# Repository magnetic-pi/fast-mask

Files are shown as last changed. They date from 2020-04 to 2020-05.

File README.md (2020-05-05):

# F.A.S.T Mask

Filter Adapted Snorkel Tube (F.A.S.T) Mask <br />
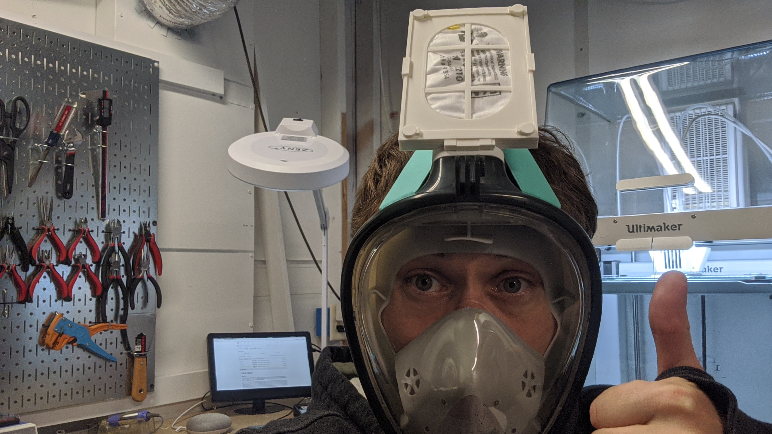
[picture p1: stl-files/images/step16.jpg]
        

#### Objective

The **Filter Adapted Snorkel Tube** (F.A.S.T) Mask is an attempt to help ease the burden facing medical staff around the world due to the shortage of face shields, eye protection, and N95 masks. The goal of this project was to find easy to obtain parts and modify them to provide a cheap reusable (PPE) mask solution.

The F.A.S.T project modifies an existing snorkel mask, so that a PM2.5, N95, P95 or other similar filters can be easily retrofitted to a modified snorkel tube. F.A.S.T provides an added advantage, as the filter masks are no longer touching a user's face directly, which helps to preserve the filters. Doctors and nurses are currently required to use the face masks for a days at a time, and that's if they are lucky enough to have access to a mask at all. The F.A.S.T solution could potentially provide a way to immediately double existing filter supplies on location, as well as increase/improve filter reusability and sharing. The F.A.S.T adapter provides an easily maintainable and reusable face shield solution for front line responders. Due to its modularity, the various parts of F.A.S.T can be quickly disassembled, sanitized, reused, and replaced. The various types of masks (N95, PM2.5) never directly touch the users face, therefore making it so masks can easily be sterilized in accordance to [sterilization studies](https://news.ycombinator.com/item?id=22680799) and reused.

Currently the Covid-19 virions are about 0.125 microns in size. This means that the PM2.5 filter may not completely protect users, however, neither will wearing an improperly fitted P95/N95 masks which often have leaks based on fit to the face. The F.A.S.T Mask also provides enhanced protection by eliminating the gaps typically found when wearing separate N95 masks, face shields, and eye protection.

This project was inspired by and is dedicated to [Dr. Usama Riaz](https://old.reddit.com/r/HumansBeingBros/comments/fnwflk/dr_usama_riaz_has_spent_weeks_screening_treating/) and the many other selfless heroes around the world who are on the front lines fighting the good fight against Covid-19.

#### Design Objectives
1. Protect users' entire face.
2. Keep the filter as isolated and clean as possible. (No facial oil contamination and mitigate direct body fluid exposure.)
3. No tooling required.
4. Easy sterilization.
5. Reusability.
6. Parts must be easily acquirable globally.
7. Provide a consistent seal between the filter and filter holder.
    
#### Build Steps
The build steps can be found in: [stl-files/INSTRUCTIONS.md](https://github.com/magnetic-pi/fast-mask/blob/master/stl-files/INSTRUCTIONS.md).

#### Licensing
The F.A.S.T components are free and open source to ensure the interoperability of F.A.S.T with various mask vendors, and to encourage rapid development by others.

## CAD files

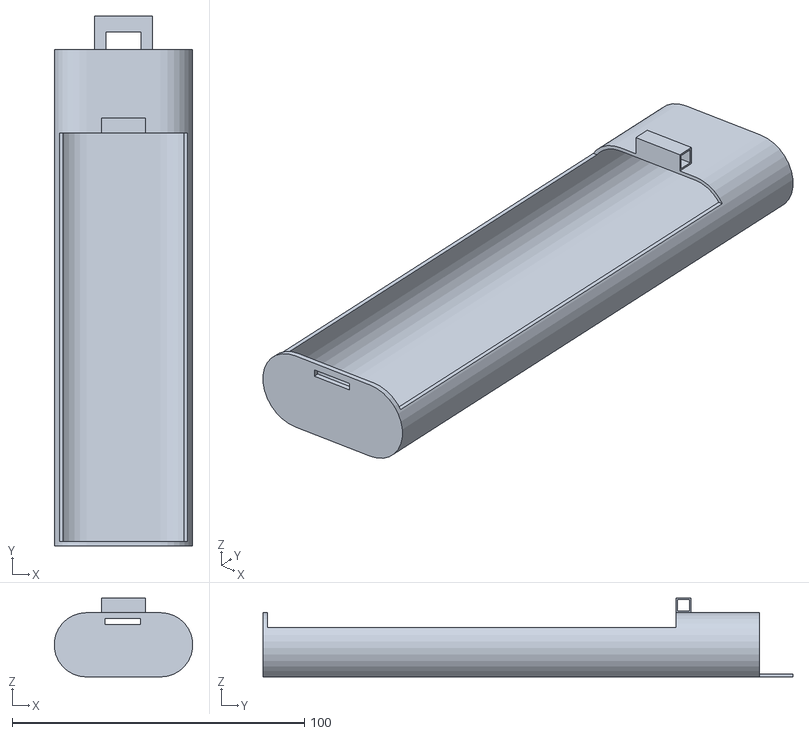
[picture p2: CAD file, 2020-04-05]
stl-files/universal-filter-mask-stl-files/snorkel-tube-connector.stl
47.4 x 181.5 x 27.0

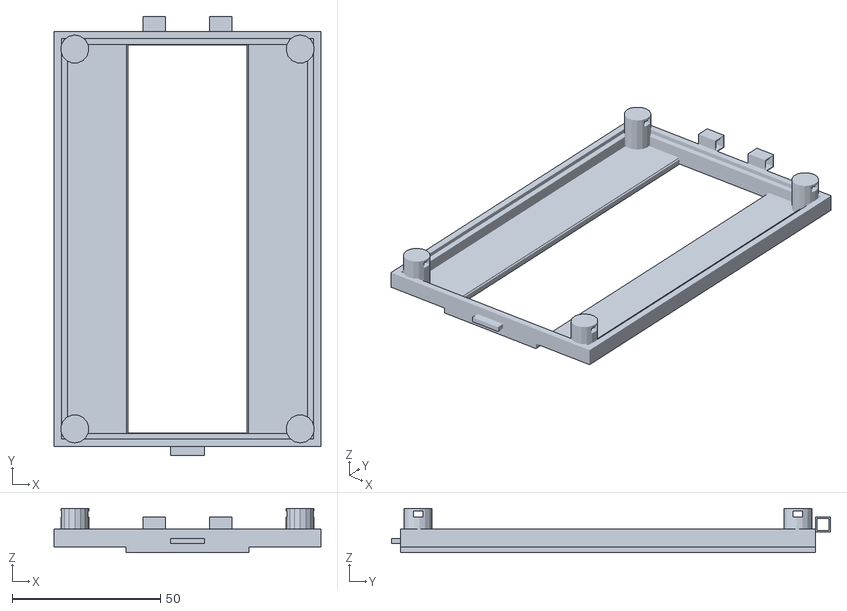
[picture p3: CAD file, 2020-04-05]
stl-files/universal-filter-mask-stl-files/filter-holder-bottom.stl
90.0 x 148.0 x 15.0

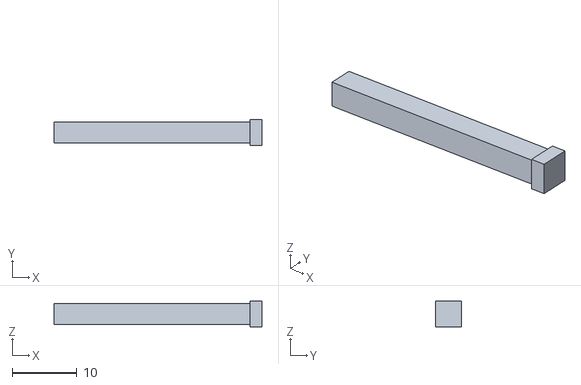
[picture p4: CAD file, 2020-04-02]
stl-files/universal-filter-mask-stl-files/connector-block-peg.stl
32.0 x 4.00 x 4.00

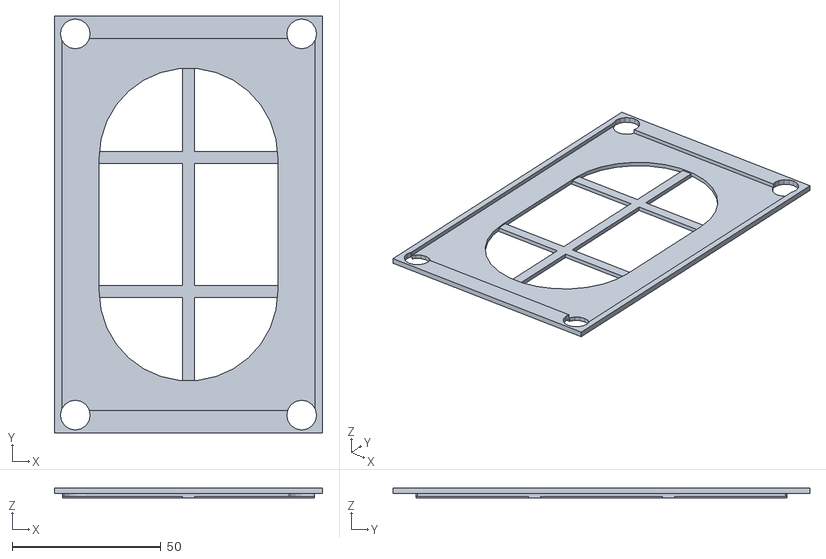
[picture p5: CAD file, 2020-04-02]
stl-files/universal-filter-mask-stl-files/universal-filter-holder.stl
90.0 x 140.0 x 3.50

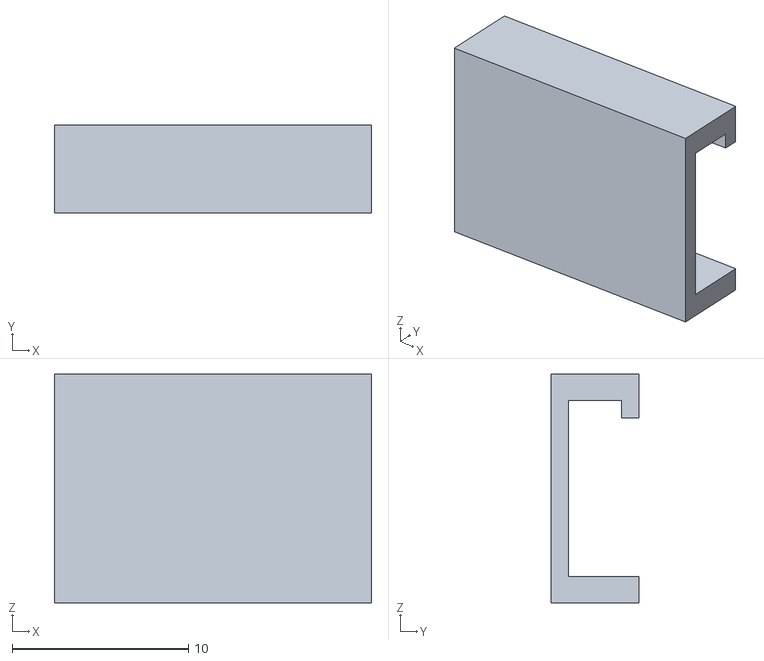
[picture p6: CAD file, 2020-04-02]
stl-files/universal-filter-mask-stl-files/filter-side-clamps.stl
18.0 x 5.00 x 13.0

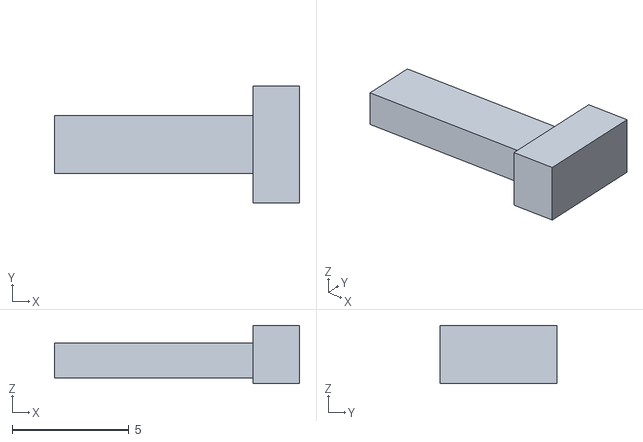
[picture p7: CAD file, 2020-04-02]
stl-files/universal-filter-mask-stl-files/peg-connector-clip.stl
10.5 x 5.00 x 2.50

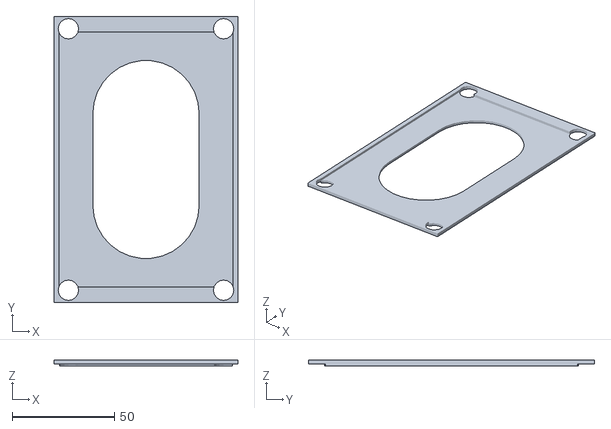
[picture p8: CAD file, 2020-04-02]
stl-files/universal-filter-mask-stl-files/front-plug.stl
90.0 x 140.0 x 3.00

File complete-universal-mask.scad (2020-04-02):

/////////////////////////////////////////////////////////////////////////
// The universal mask is made with a filter holder specifically        //
// designed to have a smaller opening to hold partial piece of a mask. //
// This should only be used in times of emergency when supplies are    //
// critically low.                                                     //
/////////////////////////////////////////////////////////////////////////


use <scad-parts/snorkel-tube-attachment.scad>
use <scad-parts/filter-holder-bottom.scad>
use <scad-parts/connector-pegs.scad>
use <scad-parts/connector-blocks.scad>
use <scad-parts/universal-filter-holder-top.scad>
use <scad-parts/front-plug.scad>
use <scad-parts/filter-side-clamps.scad>

/////////////////////////////////////////////////////
// Filter layer bottom.                            //
//use <scad-parts/filter-holder-bottom.scad>       //
/////////////////////////////////////////////////////
translate([0,1.5,-5])
filter_holder_bottom(filter_holder_top_x=90,
                     filter_holder_top_y=140,
                     filter_holder_top_z=6,
                     snorkel_diameter=25.5,
                     snorkel_tube_height=5,
                     snorkel_tube_radius=11,
                     peg_y_position=38,
                     peg_space=64,
                     number_of_pegs=2,
                     peg_height=12,
                     peg_radius=5,
                     connector_clip_x=16,
                     connector_clip_y=3,
                     connector_clip_z=2);

///////////////////////////////////////////////////////
// Universal first filter holder layer.              //
//use <scad-parts/universal-filter-holder-top.scad>  //
///////////////////////////////////////////////////////
//color("green")
//translate([0,11.50,-1])
//universal_filter_holder(filter_holder_x=90,
//              filter_holder_y=140,
//              filter_holder_z=2,
//              filter_hole_height = 6,
//              filter_hole_radius = 30,
//              filter_hole_length = 45,
//              peg_y_position=38,
//              peg_space=64,
//              number_of_pegs=2,
//              peg_height=10,
//              peg_radius=5,
//              connector_clip_x=10,
//              connector_clip_y=3,
//              connector_clip_z=2);

//////////////////////////////////////////////////////
// Universal second filter holder layer.            //
//use <scad-parts/universal-filter-holder-top.scad> //
//////////////////////////////////////////////////////
//color("red")
//translate([0,11.50,1])
//universal_filter_holder(filter_holder_x=90,
//              filter_holder_y=140,
//              filter_holder_z=2,
//              filter_hole_height = 6,
//              filter_hole_radius = 30,
//              filter_hole_length = 45,
//              peg_y_position=38,
//              peg_space=64,
//              number_of_pegs=2,
//              peg_height=10,
//              peg_radius=5,
//              connector_clip_x=10,
//              connector_clip_y=3,
//              connector_clip_z=2);

//////////////////////////////////////////////////
// Connector tube to snorkel mask.              //
//use <scad-parts/snorkel-tube-attachment.scad> //
//////////////////////////////////////////////////
rotate([0,0,0])
translate([0, 0, -5])
snorkel_filter_attachment_tube(snorkel_diameter=25.5, snorkel_tube_height=170, snorkel_tube_radius=11);

///////////////////////////////////////////
// Clips for four filter holder pegs.    //
// use <scad-parts/connector_pegs.scad>  //
///////////////////////////////////////////
//peg_connector_clip(connector_clip_x=10,
//                   connector_clip_y=2.5,
//                   connector_clip_z=1.5);

///////////////////////////////////////////
// Peg for front holder squares.         //
//use <scad-parts/connector_blocks.scad> //
///////////////////////////////////////////
//connector_block_peg(ccube_x=30, 
//                     ccube_y=4,
//                     ccube_z=4);

///////////////////////////////////////////////
// Side clamps for preventing side buldging. //
//use <scad-parts/filter-side-clamps.scad>   //
///////////////////////////////////////////////
//filter_side_clamps();

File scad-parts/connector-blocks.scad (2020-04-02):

//////////////////////////////////////////////////////////////////////////////////////////////
// This module is used for connecting the snorkel to the filter.//
//////////////////////////////////////////////////////////////////////////////////////////////

// Generates two BLUEoutside blocks for the plug to connect through.
module connector_block_cutout(ccube_x, ccube_y, ccube_z){
    color("blue")
    difference() {
        cube([ccube_x, ccube_y, ccube_z],center=true);
        cube([ccube_x+2, ccube_y-1, ccube_z-1],center=true);
    }
}

// Generates RED inside block for the plug to connect through.
module connector_block_outsides(ccube_x, ccube_y, ccube_z){
    color("red")
    difference() {
        connector_block_cutout(ccube_x, ccube_y, ccube_z);
        cube([ccube_x-15, ccube_y+2, ccube_z+2],center=true);
    }
}

// Generates the white plug to hold the parts together.
module connector_block_peg(ccube_x, ccube_y, ccube_z){
    color("white")
    difference() {
        cube([ccube_x+2, ccube_y, ccube_z],center=true);
        translate([-1, 0, 0])
        connector_block_cutout(ccube_x+.25, ccube_y+.25, ccube_z+.25);
    }
}

// Generates two BLUEoutside blocks for the plug to connect through.
connector_block_outsides(ccube_x=30, ccube_y=5, ccube_z=5);

// Generates RED inside block for the plug to connect through.
connector_block_cutout(ccube_x=15, ccube_y=5, ccube_z=5);

// Generates the white plug to hold the parts together.
//connector_block_peg(ccube_x=30, ccube_y=5, ccube_z=5);

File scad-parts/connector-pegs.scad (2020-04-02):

//////////////////////////////////////////////////////////////////
// This module is used for generating the peg cutouts and pegs. //
//////////////////////////////////////////////////////////////////

// peg_space: This controls the X-axis space between the pegs.
// number_of_pegs: This defines the number of pegs to generate.
// peg_height: This defines the Z-axis height of the peg.
// peg_radius: This determines the diameter/circumferance of each peg.
// peg_y_position: This determines the Y-axis position of the pegs.

// This generates the GREEN peg clip.
module peg_connector_clip(connector_clip_x, connector_clip_y, connector_clip_z) {
    color("green")
    cube([connector_clip_x, connector_clip_y, connector_clip_z],true);
    translate([connector_clip_y+2,0,.25])
    cube([2,5,2.5],true);
}

// This generates the WHITE hole size in the Blue peg so the GREEN clip can slide in.
module peg_connector_hole(connector_clip_x, connector_clip_y, connector_clip_z) {
    color("white")
    peg_connector_clip(connector_clip_x+.25, connector_clip_y+.25, connector_clip_z);
}

// This module combines and diffs the WHITE hole from the BLUE peg.
module peg(peg_height, peg_radius, connector_clip_x, connector_clip_y, connector_clip_z) {
    difference() {
        // This generates the BLUE peg.
        color("blue")
        cylinder(h = peg_height, r1 = peg_radius, r2 = peg_radius, center = true);
        
        // This is the WHITE peg Hole.
        rotate([0,0,90])
        translate([2, 0, +4])
        peg_connector_hole(connector_clip_x, connector_clip_y, connector_clip_z);
    }
}

// This module generates "number_of_pegs" at "pegs_space" in millimeters apart.
module holder_pegs(peg_space, number_of_pegs, peg_height, peg_radius, connector_clip_x, connector_clip_y, connector_clip_z) {
    for (i=[0: 360/number_of_pegs: 360])
        rotate([0,0,i])
        translate([peg_space,0,0])
        peg(peg_height, peg_radius, connector_clip_x, connector_clip_y, connector_clip_z);
}


peg_y_position=20;

translate([0,peg_y_position,0])
holder_pegs(peg_space=60,
            number_of_pegs=2,
            peg_height=12,
            peg_radius=5,
            connector_clip_x=13,
            connector_clip_y=3,
            connector_clip_z=2);

//translate([0,-peg_y_position,0])
//holder_pegs(peg_space=60,
//            number_of_pegs=2,
//            peg_height=12,
//            peg_radius=5,
//            connector_clip_x=10,
//            connector_clip_y=3,
//            connector_clip_z=2);

//peg_connector_clip(connector_clip_x=10,
//                   connector_clip_y=3,
//                   connector_clip_z=2);

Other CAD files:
scad-parts/filter-holder-bottom.scad
scad-parts/filter-side-clamps.scad
scad-parts/front-plug.scad
scad-parts/snorkel-tube-attachment.scad
scad-parts/universal-filter-holder-top.scad

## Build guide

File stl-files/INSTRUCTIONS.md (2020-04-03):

# F.A.S.T Mask Assembly Instructions

### Overview
These directions assume that filter (N95, P95, PM2.5) masks will need to be altered to fit in the filter holders correctly. Ideally 3M or some other manufactures would be able create a flat filter much like the PM2.5 filter [here](https://www.amazon.com/Filters-Replacement-Running-Cycling-Activities/dp/B086GS2NBW/ref=sr_1_6?crid=T60BPNRLF9CD&dchild=1&keywords=pm2.5+mask+replacement+filters&qid=1585763601&sprefix=pm2.5+mask+replacement+%2Caps%2C211&sr=8-6) so that cutting a filter masks would no longer be required. The steps outlined in this document will guide users through the process for altering a N95 mask so that it will work with the F.A.S.T appliance.

### Requirements
1. Snorkel Mask ([Amazon Link](https://www.amazon.com/Knit-Outdoor-Panoramic-Anti-Fog-Anti-Leak/dp/B079FL6W4C))
2. PM2.5 Activated Carbon Filter ([Amazon Link](https://www.amazon.com/gp/product/B086634MWS))
3. N95 or P95 Mask. (Currently out everywhere!)
4. All parts have been printed from [stl-files/universal-filter-mask-stl-files/](https://github.com/magnetic-pi/fast-mask/tree/master/stl-files/universal-filter-mask-stl-files) directory:

    * Modified Snorkel tube attachment. (Print 1)
    * Filter Holders. (Print 2)
    * Bottom Filter Holder. (Print 1)
    * Connector Pegs. (Print 4)
    * Connector Block Peg. (Print 1)

### Build Steps
1. Grab a N95 mask. <br />
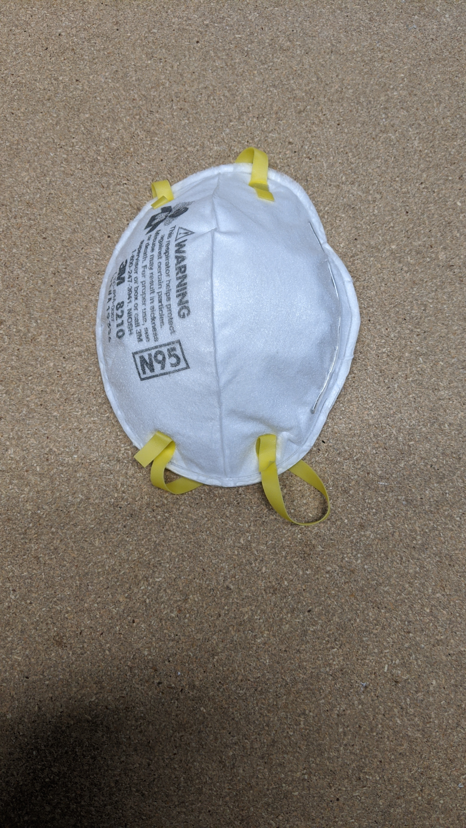
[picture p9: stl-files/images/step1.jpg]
    

2. Remove any straps on the outside of the mask.<br />
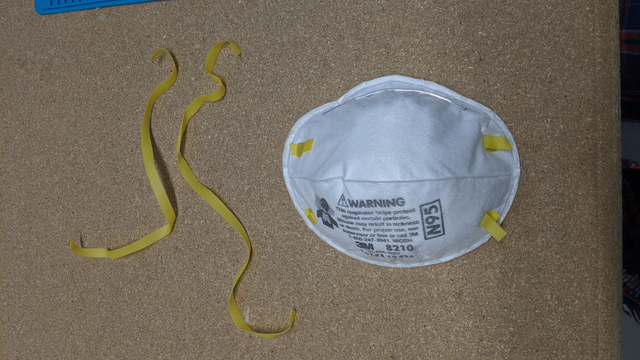
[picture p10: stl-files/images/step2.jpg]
    
    
3. Cut the mask in half.<br />
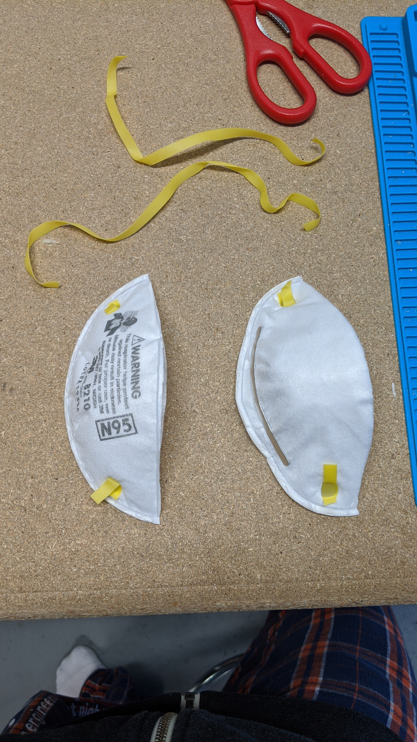
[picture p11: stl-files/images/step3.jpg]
    
    
4. Cut off the two ends so that the mask fits in the filter holder ensuring the hole is covered correctly.<br />
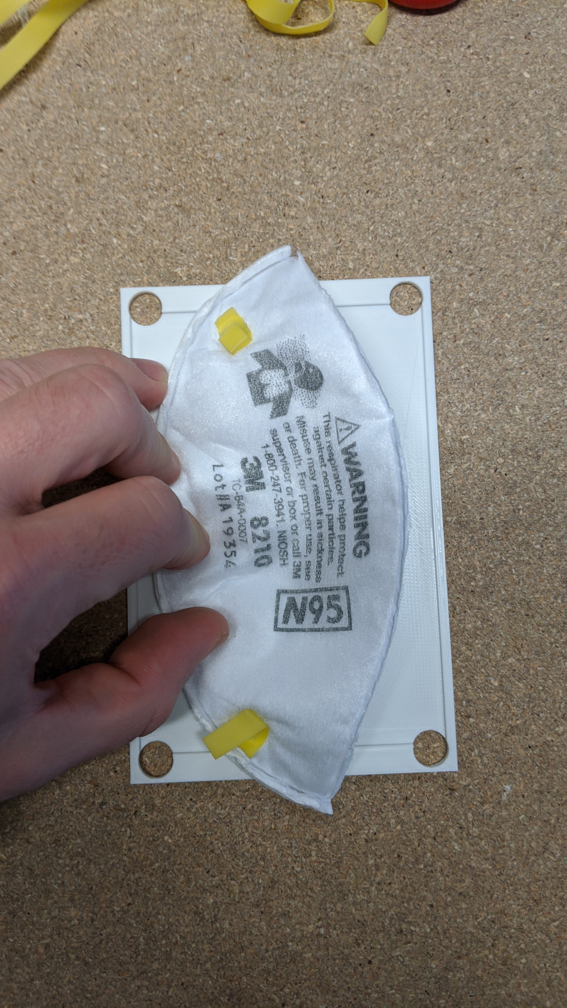
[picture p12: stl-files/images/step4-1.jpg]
    
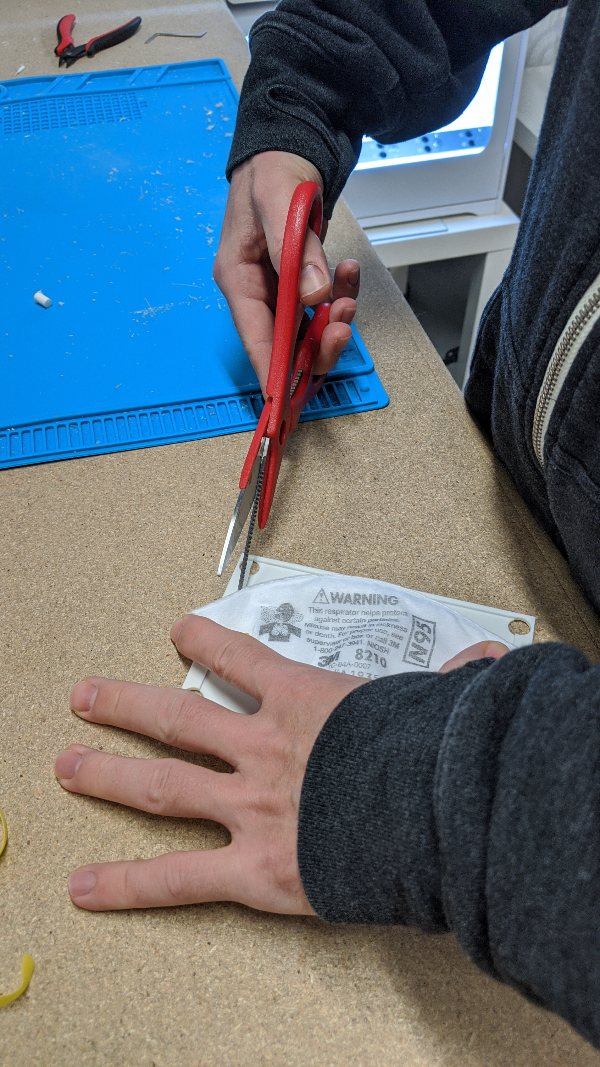
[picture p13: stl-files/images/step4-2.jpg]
    

5. Lay out the F.A.S.T parts.<br />
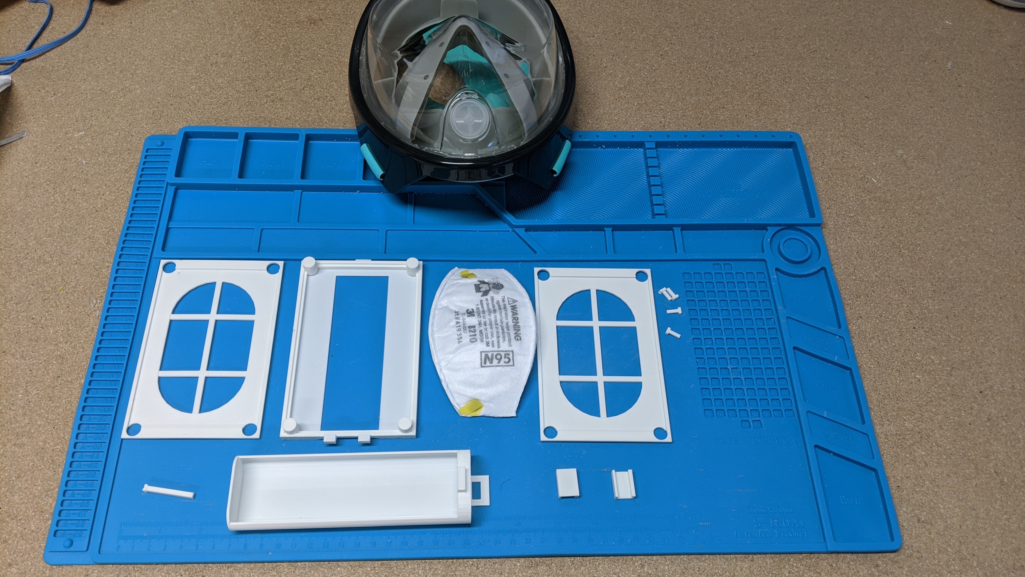
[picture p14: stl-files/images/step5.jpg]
   

6. Attach the filter holder pieces to the filter bottom.<br />
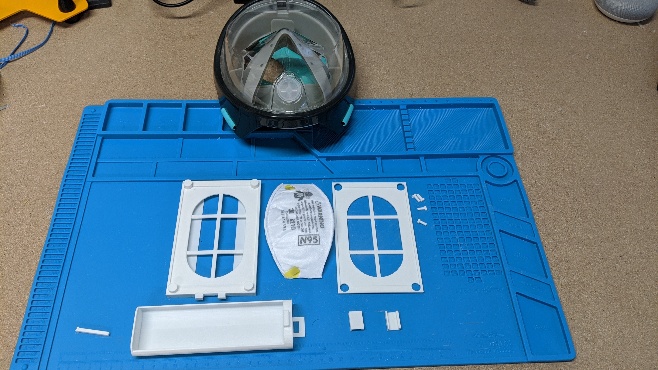
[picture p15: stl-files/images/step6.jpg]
    
    
7. Place filter on top of the first filter holder, making sure to completely cover the opening below it.<br />
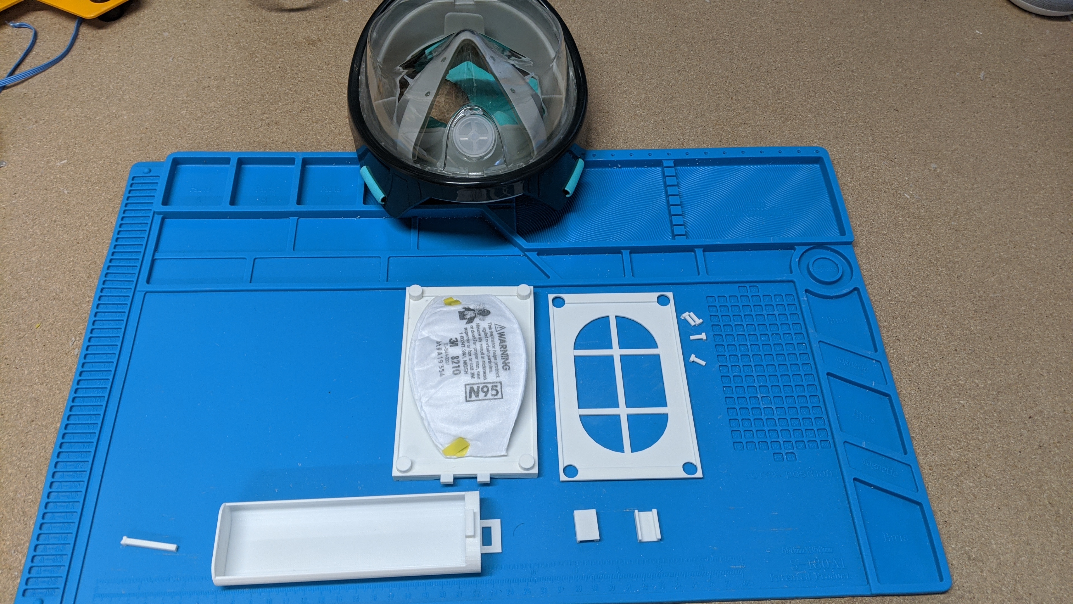
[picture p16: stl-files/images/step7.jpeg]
    
    
8. Attach the second filter holder piece on top.<br />
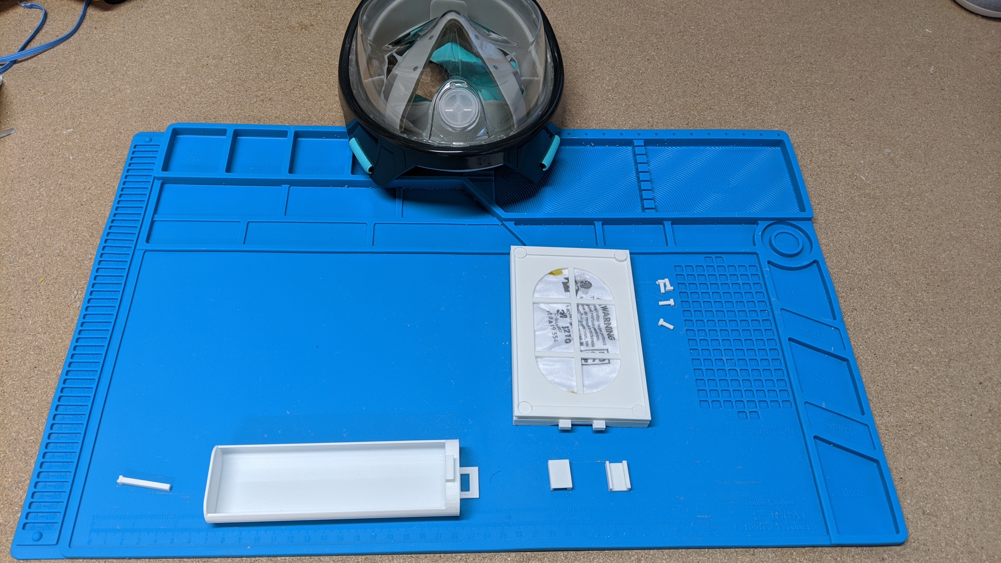
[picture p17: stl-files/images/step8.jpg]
    
    
9. Insert the filter holder pins into the four round pegs in the corners.<br />
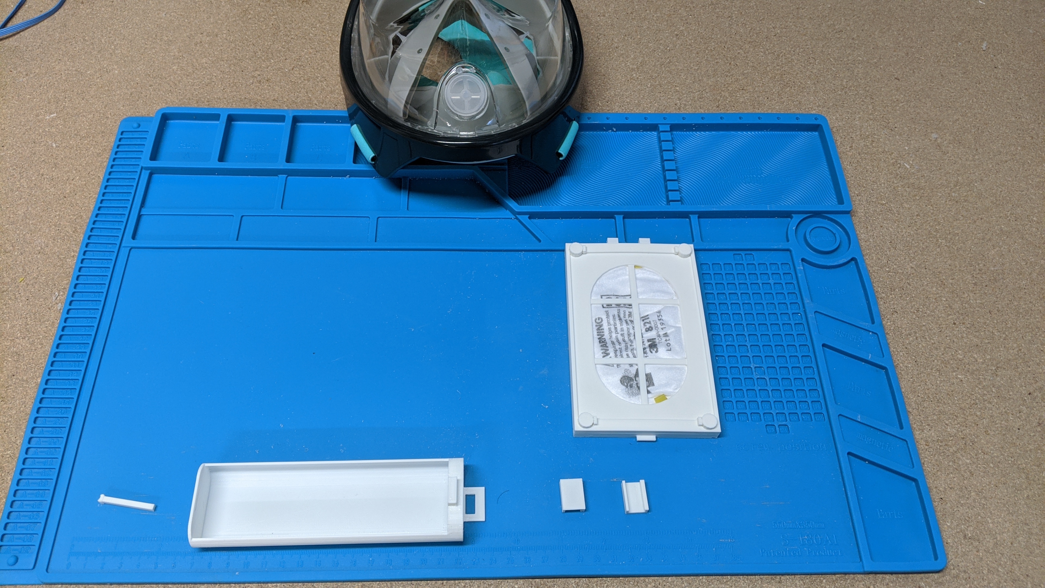
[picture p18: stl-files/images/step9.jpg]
    

10. Place filter side clamps on the sides of the filter to ensure that the filter holders are holding the filters tightly.<br />
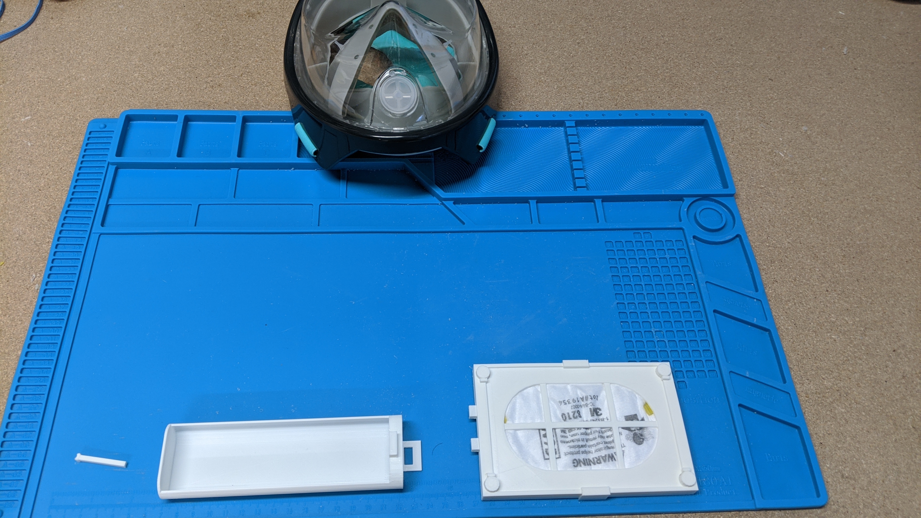
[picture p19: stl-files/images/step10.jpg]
    

11. Attach the filter bottom to the snorkel tube using the provided slots.<br />
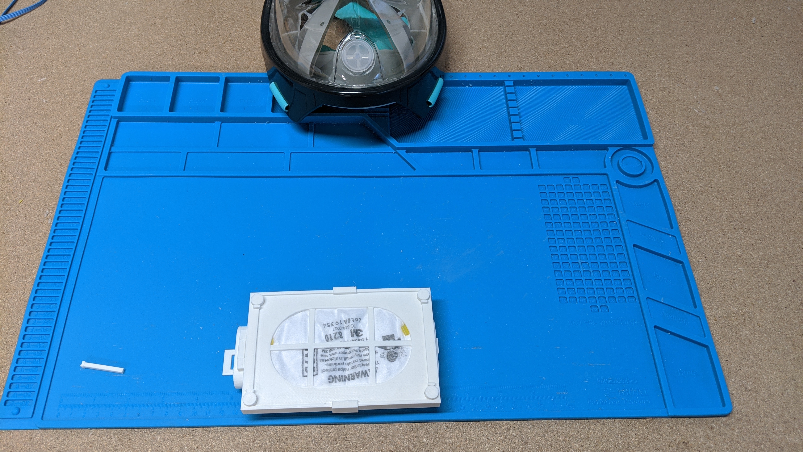
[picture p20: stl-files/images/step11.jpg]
    
    
12. Place connector block peg in the front of the filter, connecting the filter botom to the snorkel tube.<br />
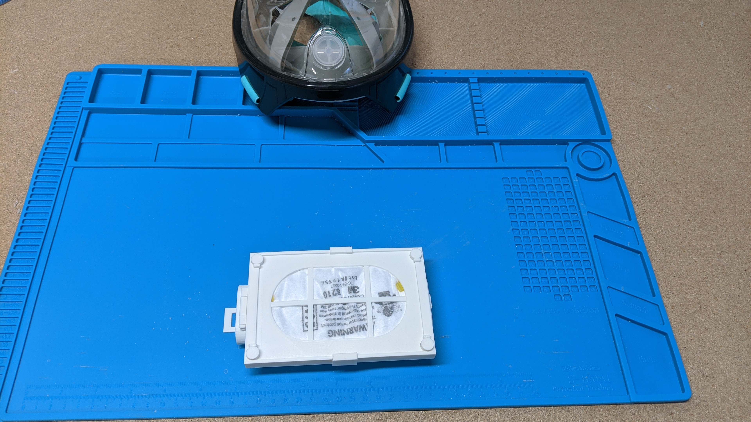
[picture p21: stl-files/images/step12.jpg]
    
    
13. Affix the F.A.S.T attachment to the snorkel tube holder on snorkel mask until it clicks into palce.<br />
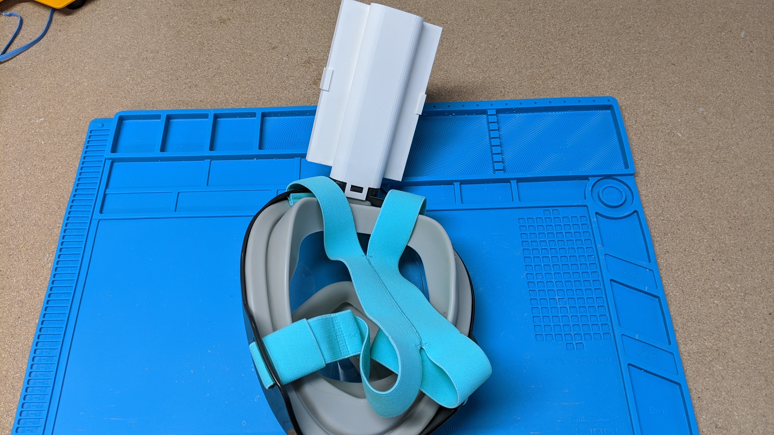
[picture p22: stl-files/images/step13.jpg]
    

14. Complete!<br />
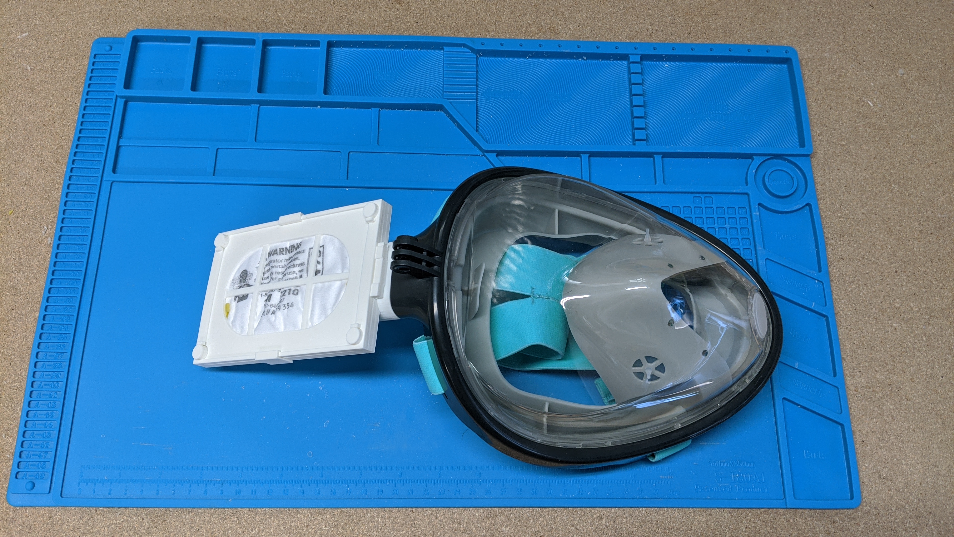
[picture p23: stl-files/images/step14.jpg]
    
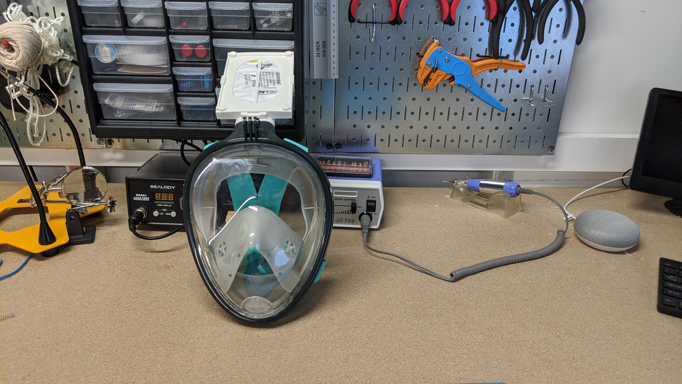
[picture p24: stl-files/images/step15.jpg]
    


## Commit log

2020-04-02 Migrating to github from local host.
    [complete-universal-mask.scad, connector-block-peg.stl, connector-blocks.scad, connector-pegs.scad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]
2020-04-05 Updated filter bottom to have a better seal and rigidity.
    [filter-holder-bottom.scad, filter-holder-bottom.stl, snorkel-tube-connector.stl]
